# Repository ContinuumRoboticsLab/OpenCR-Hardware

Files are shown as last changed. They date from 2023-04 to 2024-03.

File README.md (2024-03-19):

# OpenCR-Hardware

Here we provide CAD design, component lists, assembly instructions, and software for you to create your continuum robot.
The prototypes, parts of them, and extensions can be used to build torque-controlled continuum robot prototypes.
A paper describing the actuation module and three different derived prototypes can be found [here](https://arxiv.org/abs/2304.11850).

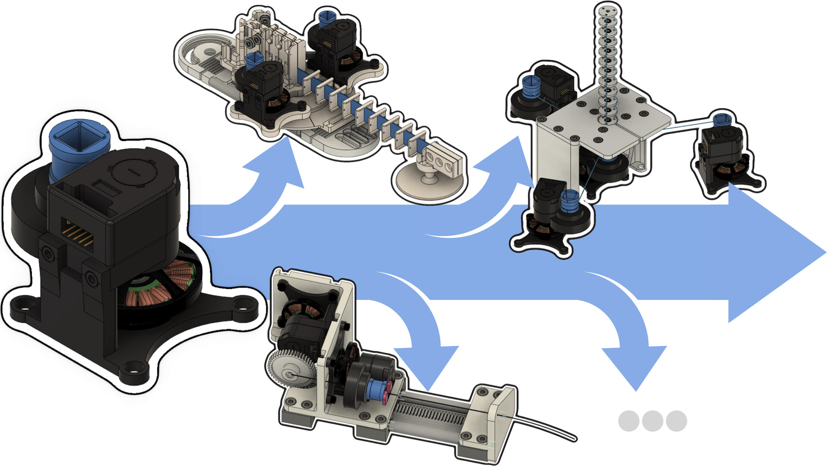
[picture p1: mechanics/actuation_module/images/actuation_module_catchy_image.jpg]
catchy overview


*Figure: An actuation module for a wide range of continuum robots*

## Electronics

| TI Evaluation Board                                                                                                       | Consumer PC | Details Wiring |  
|---------------------------------------------------------------------------------------------------------------------------|-------------|----------------|   
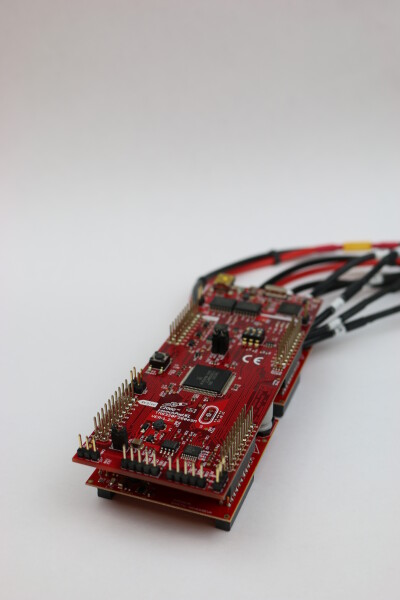
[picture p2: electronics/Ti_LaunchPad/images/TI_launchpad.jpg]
|  | WIP         | WIP            |

## Mechanics

| Concentric Tube Continuum Robot (LOTR CTCR)                                                                             | spatial Tendon-Driven Continuum Robot (LOTR TDCR)                                                                                    | parallel Tendon-Driven Continuum Robot (LOTR TDCR)                                                                                |  
|-------------------------------------------------------------------------------------------------------------------------|--------------------------------------------------------------------------------------------------------------------------------------|-----------------------------------------------------------------------------------------------------------------------------------|   
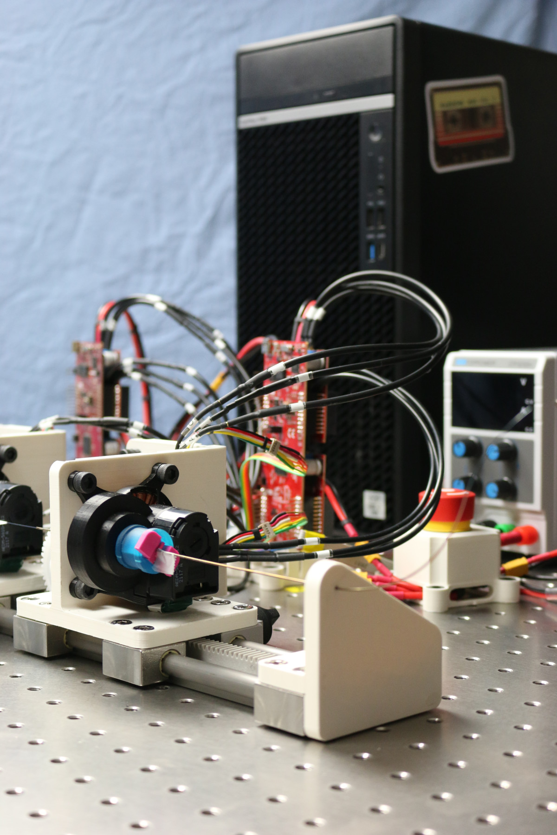
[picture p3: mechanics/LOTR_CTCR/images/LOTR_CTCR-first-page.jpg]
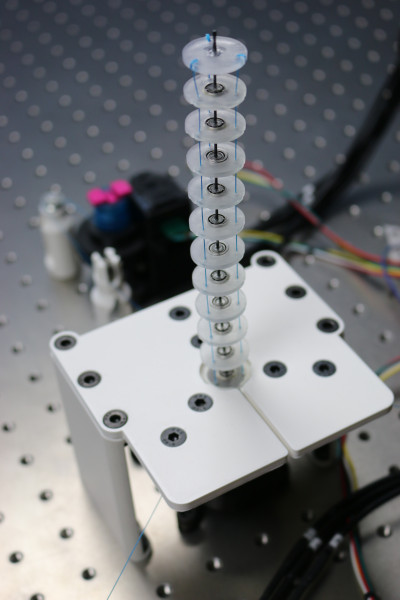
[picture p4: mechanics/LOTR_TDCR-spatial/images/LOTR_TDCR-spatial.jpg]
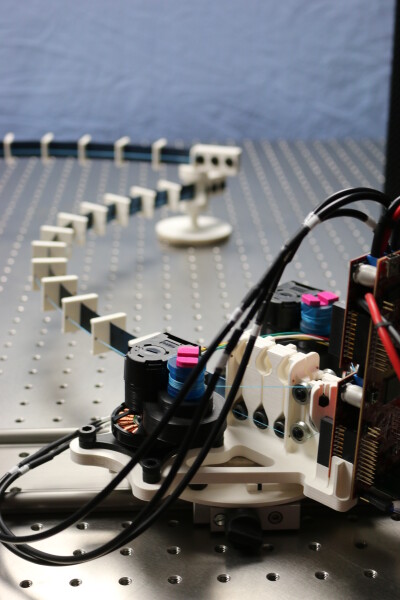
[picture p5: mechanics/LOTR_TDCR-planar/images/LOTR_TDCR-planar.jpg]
|  |  |  |

## More Information

### Further Links

[OpenCR Project](http://opencontinuumrobotics.ca)
<br/>
[Back to Top of Page](README.md)
<br/>
[Electronic Overview](electronics/README.md)
<br/>
[Hardware Overview](mechanics/README.md)

### Authors

Authors are listed in alphabetic order.

- Reinhard M. Grassmann

### License

BSD 3-Clause License

Copyright (c) 2023, Continuum Robotics Laboratory, University of Toronto

### BibTeX

This repository is part of the [OpenCR Project](http://www.opencontinuumrobotics.ca/) and different publications.
If you want to reference this project, you can use the following citation:

```bibtex
    @article{GrassmannBurgner-Kahrs_et_al_Frontiers_2023,
        title       =   {Open Continuum Robotics – One Actuation Module to Create them All},
        author      =   {Grassmann, Reinhard M. and Shentu, Chengnan and Hamoda, Taqi and Triana Dewi, Puspita and Burgner-Kahrs, Jessica},
        journal     =   {Frontiers in Robotics and AI},
        volume      =   {11},
        pages       =   {1272403},
        year        =   {2024},
        doi         =   {10.3389/frobt.2024.1272403}
    }
```
We took great inspiration from the [Open Dynamic Robot Initiative](https://open-dynamic-robot-initiative.github.io/), where efforts are made to build cost-efficient actuators for torque-controlled [legged robots](https://arxiv.org/abs/1910.00093) and [manipulators](https://arxiv.org/abs/2008.03596).

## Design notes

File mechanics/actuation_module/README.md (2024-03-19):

# OpenCR-Hardware Actuation Module

## Electronics Overview

WIP

## Mechanics Overview

WIP

### 3D Printed Parts

WIP

### Off-the-shelf Components

WIP

### Step-by-Step Instructions

WIP

## Bill of Materials for one Actuation Module

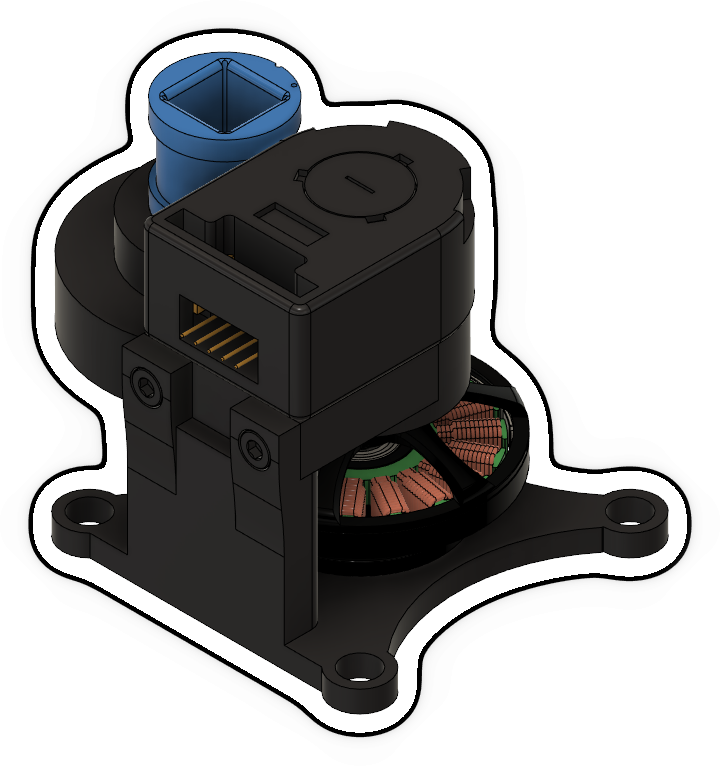
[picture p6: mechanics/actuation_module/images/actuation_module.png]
catchy overview


| Part Name                         | Quantity | Notes                                                                | File/Link                                                                                                            |  
|-----------------------------------|----------|----------------------------------------------------------------------|----------------------------------------------------------------------------------------------------------------------|   
| ActuationUnit_MotorSide_Cube      | 1        | 3D printed part ([drawing](drawings/Motor_Frame.pdf))                | [STL file](stl_files/ActuationUnit_EncoderCouplingSide.stl)                                                          |
| Motor                             | 1        | T-Motor MN4004                                                       | [External link](https://store.tmotor.com/goods-438-Antigravity+MN4004+KV300+-+2PCSSET.html)                          |
| Gear_Motor                        | 1        | McMaster Carr (P/N 2662N313)                                         | [External link](https://www.mcmaster.com/2662N313/)                                                                  |
| Gear_Encoder                      | 1        | McMaster Carr (P/N 2662N321)                                         | [External link](https://www.mcmaster.com/2662N321/)                                                                  |
| ActuationUnit_EncoderCouplingSide | 1        | 3D printed part ([drawing](drawings/Encoder_Frame.pdf))              | [STL file](stl_files/ActuationUnit_MotorSide_Cube.stl)                                                               |
| Ball Bearing                      | 2        | McMaster Carr (P/N 5972K910)                                         | [External link](https://www.mcmaster.com/5972K91/)                                                                   |
| Shaft_GearCoupling                | 1        | 3D printed part ([drawing](drawings/Shaft_GearCoupling_Drawing.pdf)) | [STL file](stl_files/Shaft_GearCoupling.stl)                                                                         |
| Shaft_MotorEncoder                | 1        | 3D printed part ([drawing](Shaft_MotorEncoder_Drawing.pdf))          | [STL file](stl_files/Shaft_MotorEncoder.stl)                                                                         |
| Screw M3x10                       | 2        | McMaster Carr (P/N 91290A115)                                        | [External link](https://www.mcmaster.com/91290A115/)                                                                 |
| Nut M3                            | 2        | McMaster Carr (P/N 90593A001)                                        | [External link](https://www.mcmaster.com/90593A001/)                                                                 |
| Encoder                           | 1        | Avago AEDM-5810                                                      | [External link](https://www.mouser.ca/ProductDetail/Broadcom-Avago/AEDM-5810-Z12?qs=nm95cbFn36yryX%2Fd2Onjlw%3D%3D ) |

## More Information

### Further Links

[OpenCR Project](http://opencontinuumrobotics.ca)
<br/>
[Back to Top of Page](README.md)
<br/>
[Electronic Overview](electronics/README.md)
<br/>
[Hardware Overview](mechanics/README.md)

### Authors

Authors are listed in alphabetic order.

- Puspita Triana Dewi
- Reinhard M. Grassmann

### License

BSD 3-Clause License

Copyright (c) 2023, Continuum Robotics Laboratory, University of Toronto

### BibTeX

This design is part of the [OpenCR Project](http://www.opencontinuumrobotics.ca/).
If you want to reference this design, you can use the following citation:

```bibtex
    @article{GrassmannBurgner-Kahrs_et_al_Frontiers_2023,
        title       =   {Open Continuum Robotics – One Actuation Module to Create them All},
        author      =   {Grassmann, Reinhard M. and Shentu, Chengnan and Hamoda, Taqi and Triana Dewi, Puspita and Burgner-Kahrs, Jessica},
        journal     =   {Frontiers in Robotics and AI},
        volume      =   {11},
        pages       =   {1272403},
        year        =   {2024},
        doi         =   {10.3389/frobt.2024.1272403}
    }
```

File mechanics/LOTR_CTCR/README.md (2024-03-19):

# Concentric Tube Continuum Robot Prototype

Concentric tube continuum robots (CTCR) are a class of continuum robots.
A CTCR consists of multiple nested tubes that are concentric, pre-curved, and super-elastic. 
To generate a motion by changing the centerline of the nested tubes, each tube can be rotated and translated.
The rotational and translational motion can be generated by using two independent motors attached to a carriage. 
We refer to the survey by [Nwafor, Rabenorosoa et al. (T-RO 2023)](https://doi.org/10.1109/TRO.2023.3255512) for a general overview on CTCRs. 

We developed a torque-controlled CTCR with low complexity.
It is shown in the image below.

<p float="left">
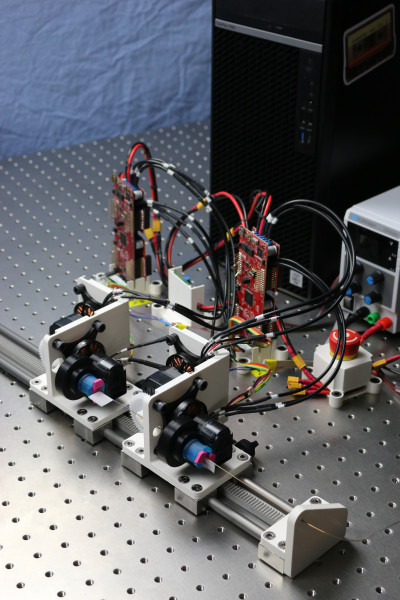
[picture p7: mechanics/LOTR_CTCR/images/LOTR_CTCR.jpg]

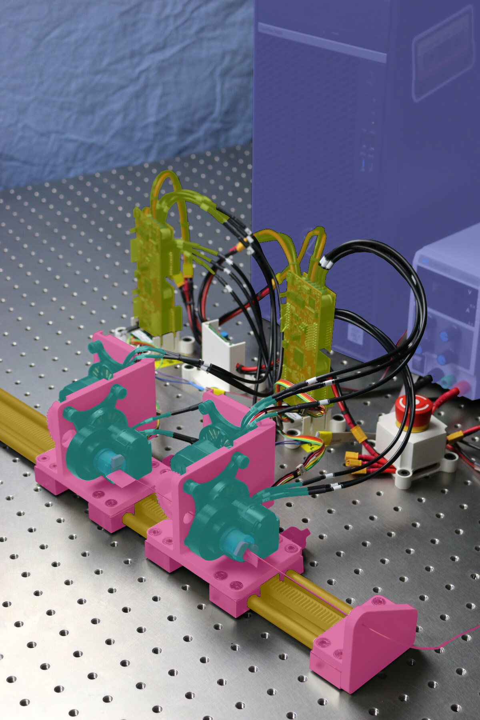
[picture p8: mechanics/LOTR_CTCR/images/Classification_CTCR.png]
classification overview

</p>

*Figure: Image of a CTCR with two carriages. Right images shows a classification of the component. (cyan) actuation modules, (red) frames, (yellow) guiding rail, (green) evaluation boards, and (blue) consumer pc with power supply.*

## Electronics Overview

WIP

## Mechanics Overview

WIP

### Tubes

Note that we do not provide tubes.
In general, the flexible tubes are made of a Nitinol or made of thermoplastic materials in some instances. 
The material can be arbitrary as long as the elastic interaction between the tubes can be exploited.
For example

- Thermoplastic material [Amanov, Nguyen & Burgner-Kahrs (SPIE 2015)](https://doi.org/10.1117/12.2081999) and [Morimoto & Okamura (T-RO 2016)](https://doi.org/10.1109/TRO.2016.2602368)
- Nitinol [Sears & Dupont (IROS 2006)](https://doi.org/10.1109/IROS.2006.282072) and [Webster, Okamura & Cowan (IROS 2006)](https://doi.org/10.1109/IROS.2006.282073)

Further references are provided in [Nwafor, Rabenorosoa et al. (T-RO 2023)](https://doi.org/10.1109/TRO.2023.3255512). 
    
We ordered our pre-curved Nitinol tubes from [Euroflex GmbH (Nuernberg, Germany)](https://www.euroflex.de/en/index.html).

### 3D Printed Parts

WIP

### Off-the-shelf Components

WIP

### Bill of Materials for Concentric Tube Continuum Robot Prototype

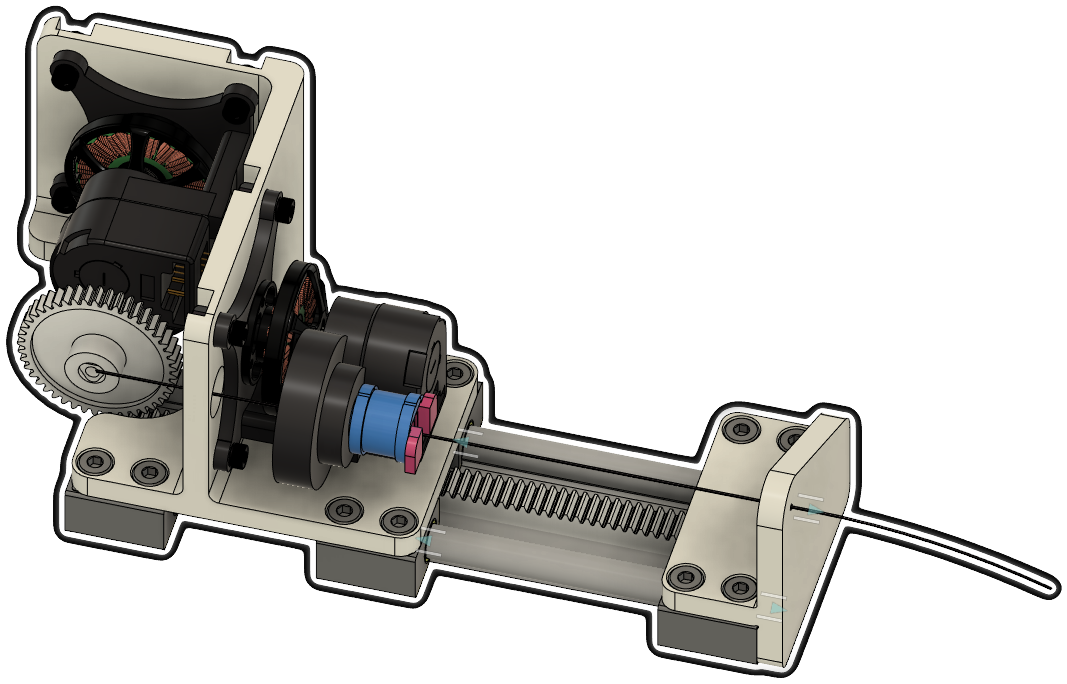
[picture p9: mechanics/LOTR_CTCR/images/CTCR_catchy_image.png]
catchy overview


| Part Name            | Quantity | Notes                                                           | File/Link                                                                                            |  
|----------------------|----------|-----------------------------------------------------------------|------------------------------------------------------------------------------------------------------|   
| Actuation Module     | 2        |                                                                 | [Link](https://github.com/ContinuumRoboticsLab/OpenCR-Hardware/tree/main/mechanics/actuation_module) |
| Main_Frame           | 1        | 3D printed part ([drawing](drawings/Main_Frame_drawing.pdf))    | [STL file](stl_files/Main_Frame.stl)                                                                 |
| Front_Frame          | 1        | 3D printed part ([drawing](drawings/Front_Frame_drawing.pdf))   | [STL file](stl_files/Front_Frame.stl)                                                                |
| Cap Gear             | 1        | 3D printed part ([drawing](drawings/Cap_Gear_8mm_drawing.pdf))  | [STL file](stl_files/Cap_Gear_8mm.stl)                                                               |
| Tube Cap             | 1        | 3D printed part ([drawing](drawings/Tube_coppling_drawing.pdf)) | [STL file](stl_files/Tube_Cap.stl)                                                                   |
| Rail                 | 1        | Igus (P/N WS-10-40))                                            | [External Link](https://www.igus.eu/product/732?artNr=WS-10-40)                                      |
| Pillow Block         | 6        | Igus (P/N WJ200UM-01-10-AL)                                     | [External Link](https://www.igus.ca/product/1165?artNr=WJ200UM-01-10-AL)                             |
| Gear Rack            | 1        | McMaster-Carr (P/N 2662N57)                                     | [External Link](https://www.mcmaster.com/2662N57/)                                                   |
| Gear                 | 1        | McMaster-Carr (P/N 2662N42)                                     | [External Link](https://www.mcmaster.com/2662N42/)                                                   |
| M6x14 Screw          | 20       | McMaster-Carr (P/N 91290A319)                                   | [External Link](https://www.mcmaster.com/91290A319/)                                                 |
| M6 Nut               | 8        | McMaster-Carr (P/N 90593A005)                                   | [External Link](https://www.mcmaster.com/90593A005/)                                                 |
| Pre-curved NiTi Tube | 1        | Euroflex                                                        | [External Link](https://www.euroflex.de/en/index.html)                                               |

## Step-by-Step Instructions

Step 1: Assemble the [gear rack](https://www.mcmaster.com/2662N57/) onto the [rail](https://www.igus.eu/product/732?artNr=WS-10-40).

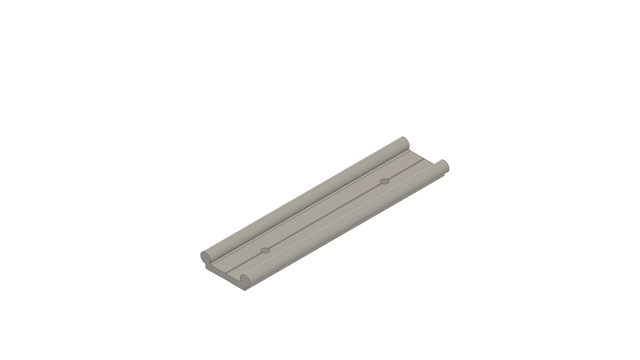
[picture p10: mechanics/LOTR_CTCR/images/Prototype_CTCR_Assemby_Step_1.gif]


Step 2: Assemble 4 [pillow blocks](https://www.igus.ca/product/1165?artNr=WJ200UM-01-10-AL) onto the rail. 

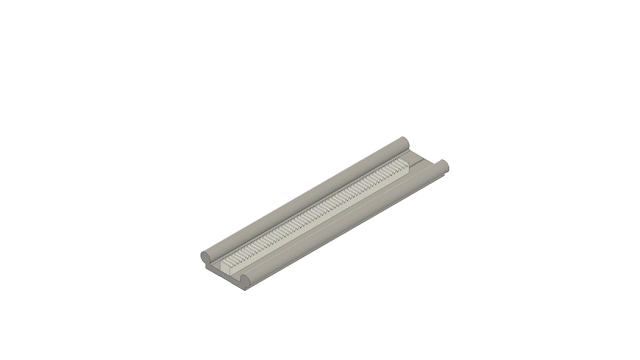
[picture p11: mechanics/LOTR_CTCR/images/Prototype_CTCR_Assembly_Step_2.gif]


Step 3: Assemble the [main frame](stl_files/Main_Frame.stl) to the rail system with 8 [M6x14 screws](https://www.mcmaster.com/91290A319/).

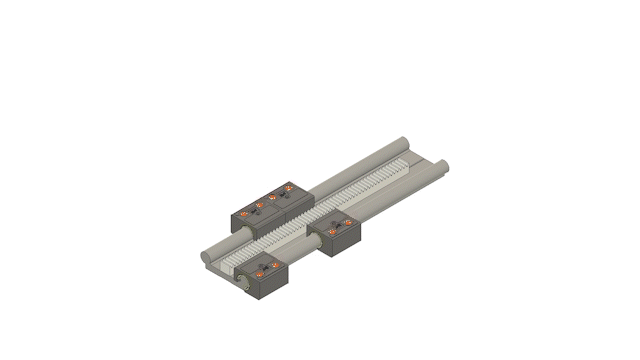
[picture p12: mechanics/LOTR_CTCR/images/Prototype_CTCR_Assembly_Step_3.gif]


Step 4: Assemble 2 [actuation modules](https://github.com/ContinuumRoboticsLab/OpenCR-Hardware/tree/main/mechanics/actuation_module) to the main frame with 4 [M6x14 screws](https://www.mcmaster.com/91290A319/) and 4 [M6 nuts](https://www.mcmaster.com/90593A005/) for each actuation module.

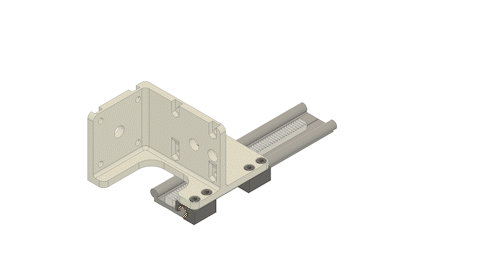
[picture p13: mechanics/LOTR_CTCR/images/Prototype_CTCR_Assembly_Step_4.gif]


Step 5: Assemble the [gear](https://www.mcmaster.com/2662N42/) to the rear actuation module using the [cap gear](stl_files/Cap_Gear_8mm.stl).

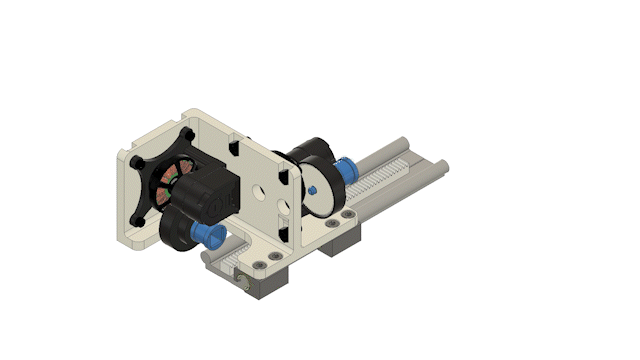
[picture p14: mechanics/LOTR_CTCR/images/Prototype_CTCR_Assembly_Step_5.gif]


Step 6: Assemble the [front frame](stl_files/Front_Frame.stl) to the rail system with 8 [M6x14 screws](https://www.mcmaster.com/91290A319/).

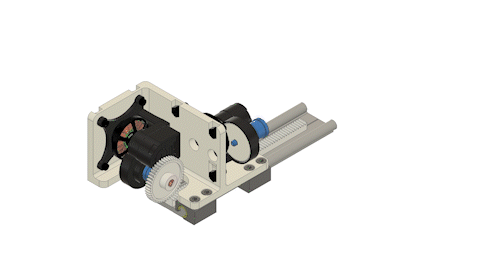
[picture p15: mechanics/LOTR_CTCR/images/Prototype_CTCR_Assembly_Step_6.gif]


Step 7: Assemble the [pre-curved Nitinol tube](https://www.euroflex.de/en/index.html) to the front actuation module using the [tube cap](stl_files/Tube_Cap.stl).

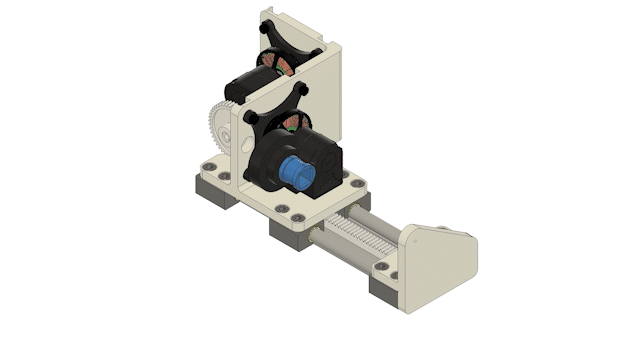
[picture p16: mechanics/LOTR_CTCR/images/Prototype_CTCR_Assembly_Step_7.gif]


## More Information

### Further Links

[OpenCR Project](http://opencontinuumrobotics.ca)
<br/>
[Back to Top of Page](README.md)
<br/>
[Electronic Overview](electronics/README.md)
<br/>
[Hardware Overview](mechanics/README.md)

### Authors

Authors are listed in alphabetic order.

- Puspita Triana Dewi
- Reinhard M. Grassmann

### License

BSD 3-Clause License

Copyright (c) 2023, Continuum Robotics Laboratory, University of Toronto

### BibTeX

This design is part of the [OpenCR Project](http://www.opencontinuumrobotics.ca/).
If you want to reference this design, you can use the following citation:

```bibtex
    @article{GrassmannBurgner-Kahrs_et_al_Frontiers_2023,
        title       =   {Open Continuum Robotics – One Actuation Module to Create them All},
        author      =   {Grassmann, Reinhard M. and Shentu, Chengnan and Hamoda, Taqi and Triana Dewi, Puspita and Burgner-Kahrs, Jessica},
        journal     =   {Frontiers in Robotics and AI},
        volume      =   {11},
        pages       =   {1272403},
        year        =   {2024},
        doi         =   {10.3389/frobt.2024.1272403}
    }
```

### Trivia

LOTR stands for Lord of the Ring, in reference to the title of the paper. Yes, the movie.

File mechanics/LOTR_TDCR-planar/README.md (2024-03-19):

# Planar Tendon-Driven Continuum Robot Prototype

A parallel continuum robot (PCR) tries to combine the world of rigid parallel robots and continuum robots.
This one is a planar PCR, where the beam is tendon-actuated.
It has two bases rigid linked at the distal end of the beam.

<p float="left">
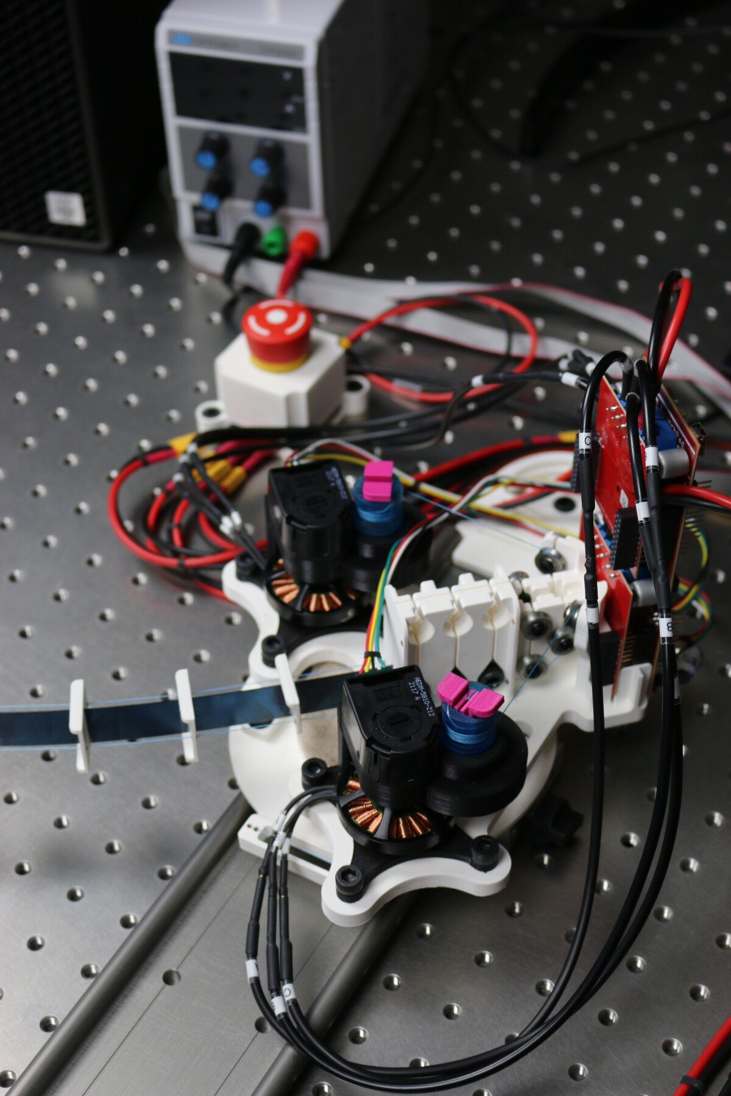
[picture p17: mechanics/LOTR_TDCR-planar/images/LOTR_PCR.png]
catchy overview

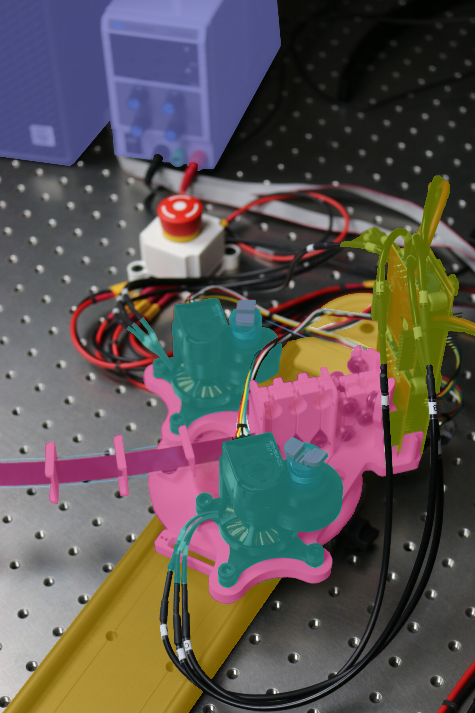
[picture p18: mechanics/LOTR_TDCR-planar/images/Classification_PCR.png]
classification overview

</p>

*Figure: Image of one base of the PCR. Right images shows a classification of the component. (cyan) actuation modules, (red) frames, (green) evaluation boards, (yellow) guiding rail, and (blue) consumer pc with power supply.*

## Electronics Overview

WIP

## Mechanics Overview

WIP

### 3D Printed Parts

WIP

### Off-the-shelf Components

WIP

### Step-by-Step Instructions

WIP

### Bill of Materials for Planar Tendon-Driven Continuum Robot Prototype 

| Part Name                       | Quantity | Notes                                                                        | File/Link                                                                                                                                                                                                                    |  
|---------------------------------|----------|------------------------------------------------------------------------------|------------------------------------------------------------------------------------------------------------------------------------------------------------------------------------------------------------------------------|   
| Actuation Module                | 2        |                                                                              | [Link](https://github.com/ContinuumRoboticsLab/OpenCR-Hardware/tree/main/mechanics/actuation_module)                                                                                                                         |
| Turret Frame                    | 1        | 3D printed part ([drawing](drawings/Frame_turret_drawing.pdf))               | [STL file](stl_files/frame_turret.stl)                                                                                                                                                                                       |
| Base Plate                      | 1        | 3D printed part ([drawing](drawings/Frame_base_plate_drawing.pdf))           | [STL file](stl_files/frame_base_plate.stl)                                                                                                                                                                                   |
| Glider                          | 1        | 3D printed part ([drawing](drawings/EE_glider_small_drawing.pdf))            | [STL file](stl_files/EE_glider_small.stl)                                                                                                                                                                                    |
| Spacer Disk                     | 9        | 3D printed part ([drawing](drawings/Spacer_Disk_drawing.pdf))                | [STL file](stl_files/spacer_disk.stl)                                                                                                                                                                                        |
| End Effector                    | 1        | 3D printed part ([drawing](drawings/EE_middle_drawing.pdf))                  | [STL file](stl_files/EE_middle.stl)                                                                                                                                                                                          |
| Rail-to-Table Connector (Right) | 1        | 3D printed part ([drawing](drawings/rail2table_connector_right_drawing.pdf)) | [STL file](stl_files/rail2table_connector_right.stl)                                                                                                                                                                         |
| Rail-to-Table Connector (Left)  | 1        | 3D printed part ([drawing](drawings/Rail2table_connector_left_drawing.pdf))  | [STL file](stl_files/rail2table_connector_left.stl)                                                                                                                                                                          |
| Felt Pad                        | 1        | Off-the-shelf component (Amazon)                                             | [External Link](https://www.amazon.ca/Scotch-SP828-NA-Round-Furniture-Brown/dp/B01MTMXCGC/ref=sr_1_4?crid=2CS0CEP2WS7PA&keywords=felt%2Bpads%2B3%22&qid=1685066557&s=hi&sprefix=felt%2Bpads%2B3%2B%2Ctools%2C89&sr=1-4&th=1) |
| Pulley                          | 8        | Off-the-shelf component (Amazon)                                             | [External Link](https://www.amazon.ca/V623ZZ-Groove-Bearing-Carbon-3x12x4mm/dp/B07CV8CW1F)                                                                                                                                   |
| Rail                            | 1        | Igus (P/N WS-10-40)                                                          | [External Link](https://www.igus.eu/product/732?artNr=WS-10-40)                                                                                                                                                              |
| Pillow Block                    | 4        | Igus (P/N WJ200UM-01-10-AL)                                                  | [External Link](https://https://www.igus.ca/product/1165?artNr=WJ200UM-01-10-AL)                                                                                                                                             |
| M6x14 Screw                     | 12       | McMaster-Carr (P/N 91290A319)                                                | [External Link](https://www.mcmaster.com/91290A319/)                                                                                                                                                                         |
| M6 Nut                          | 8        | McMaster-Carr (P/N 90593A005)                                                | [External Link](https://www.mcmaster.com/90593A005/)                                                                                                                                                                         |
| Beam                            | 1        | McMaster-Carr (P/N 9075K79)                                                  | [External Link](https://www.mcmaster.com/9075K79/)                                                                                                                                                                           |
| Tendon                          | 2        | McMaster-Carr (P/N 9442T4)                                                   | [External Link](https://www.mcmaster.com/9442T4/)                                                                                                                                                                            |

## More Information

### Further Links

[OpenCR Project](http://opencontinuumrobotics.ca)
<br/>
[Back to Top of Page](README.md)
<br/>
[Electronic Overview](electronics/README.md)
<br/>
[Hardware Overview](mechanics/README.md)

### Authors

Authors are listed in alphabetic order.

- Puspita Triana Dewi
- Reinhard M. Grassmann

### License

BSD 3-Clause License

Copyright (c) 2023, Continuum Robotics Laboratory, University of Toronto

### BibTeX

This design is part of the [OpenCR Project](http://www.opencontinuumrobotics.ca/).
If you want to reference this design, you can use the following citation:

```bibtex
    @article{GrassmannBurgner-Kahrs_et_al_Frontiers_2023,
        title       =   {Open Continuum Robotics – One Actuation Module to Create them All},
        author      =   {Grassmann, Reinhard M. and Shentu, Chengnan and Hamoda, Taqi and Triana Dewi, Puspita and Burgner-Kahrs, Jessica},
        journal     =   {Frontiers in Robotics and AI},
        volume      =   {11},
        pages       =   {1272403},
        year        =   {2024},
        doi         =   {10.3389/frobt.2024.1272403}
    }
```

### Trivia

LOTR stands for Lord of the Ring, in reference to the title of the paper. Yes, the movie.

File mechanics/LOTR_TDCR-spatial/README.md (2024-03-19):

# Spatial Tendon-Driven Continuum Robot Prototype

A tendon-driven continuum robot (TDCR) is composed of a flexible backbone along which tendons are guided using spacer disks, these last ones being fixed to the backbone. 
It is actuated by changing the tendons’ length and applying tendon tensions, which cause a reversible deformation of the backbone.
This one has one [type-II segment](https://www.frontiersin.org/articles/10.3389/frobt.2022.873446/full) and three tendons.

<p float="left">
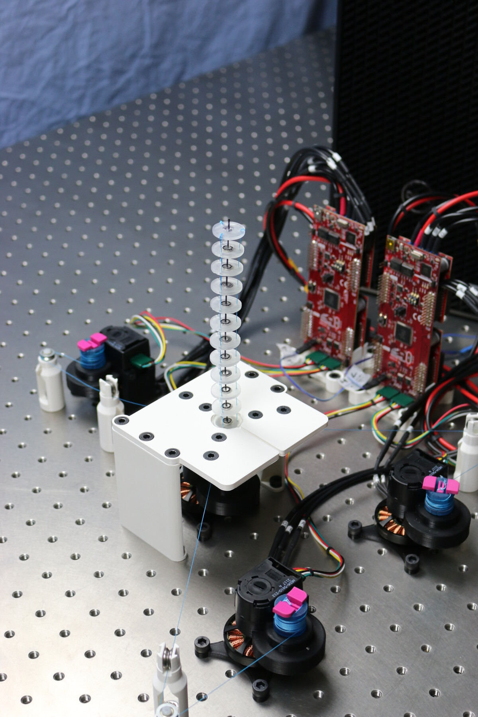
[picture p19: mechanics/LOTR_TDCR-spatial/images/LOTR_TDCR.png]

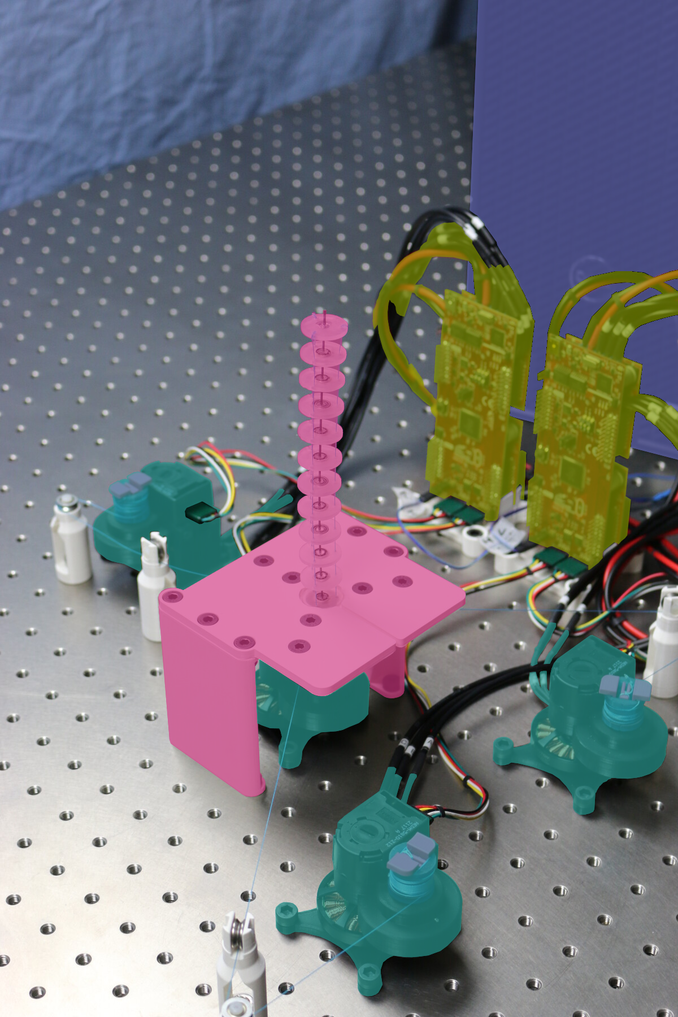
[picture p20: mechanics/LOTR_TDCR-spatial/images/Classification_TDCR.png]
classification overview

</p>

*Figure: Image of a TDCR with three degrees of freedom. Right images shows a classification of the component. (cyan) actuation modules, (red) frames, (green) evaluation boards, and (blue) consumer pc with power supply.*

## Electronics Overview

WIP

## Mechanics Overview

WIP

## 3D Printed Parts

WIP

## Off-the-shelf Components

WIP

## Bill of Materials for Spatial Tendon-Driven Continuum Robot Prototype

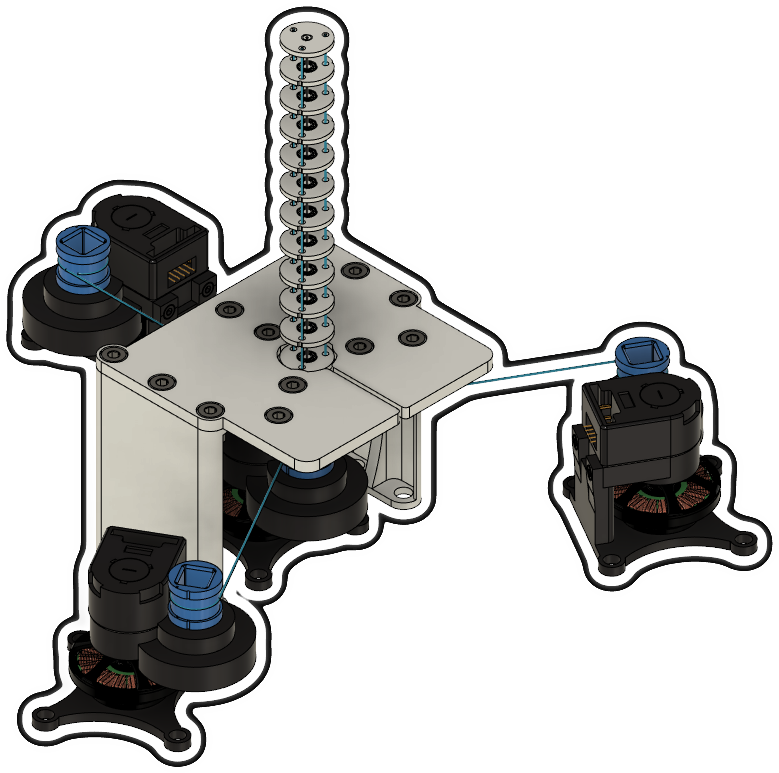
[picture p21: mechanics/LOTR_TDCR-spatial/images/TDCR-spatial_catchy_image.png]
catchy overview


| Part Name            | Quantity | Notes                                                                          | File/Link                                                                                            |  
|----------------------|----------|--------------------------------------------------------------------------------|------------------------------------------------------------------------------------------------------|   
| Actuation Module     | 4        |                                                                                | [Link](https://github.com/ContinuumRoboticsLab/OpenCR-Hardware/tree/main/mechanics/actuation_module) |
| Base Platform        | 1        | 3D printed part ([drawing](drawings/BasePlatform_drawing.pdf))                 | [STL file](stl_files/BasePlatform.stl)                                                               |
| Base Platform Wall   | 2        | 3D printed part ([drawing](drawings/BasePlatform_wall_drawing.pdf))            | [STL file](stl_files/BasePlatform_wall.stl)                                                          |
| Pulley Holder        | 3        | 3D printed part ([drawing](drawings/BasePlatform_PullyHolder_Drawing.pdf))     | [STL file](stl_files/BasePlatform_PullyHolder.stl)                                                   |
| Pulley Shaft         | 6        | 3D printed part ([drawing](drawings/Shaft_pulley_drawing.pdf))                 | [STL file](stl_files/BasePlatform_PulleyShaft.stl)                                                   |
| Disk without Dent    | 1        | 3D printed part ([drawing](drawings/FSD_20mm_bearing_withoutDent_Drawing.pdf)) | [STL file](stl_files/FSD_20mm_bearing_withoutDent.stl)                                               |
| Disk                 | 10       | 3D printed part ([drawing](drawings/Disk_drawing v1.pdf))                      | [STL file](stl_files/FSD_20mm_bearing.stl)                                                           |
| End Disk             | 1        | 3D printed part ([drawing](drawings/FSDzero_20mm_withoutDent_drawing.pdf))     | [STL file](stl_files/FSDzero_20mm.stl)                                                               |
| Inner Disk           | 12       | 3D printed part ([drawing](drawings/FSD_bearing_inner_Drawing.pdf))            | [STL file](stl_files/FSD_bearing_inner.stl)                                                          |
| Tube Coupling        | 1        | 3D printed part ([drawing](drawings/Tube_coppling_1mm_drawing.pdf))            | [STL file](stl_files/Tube_coppling_1mm.stl)                                                          |
| Bearing              | 11       | McMaster-Carr (P/N 57155K438)                                                  | [External link](https://www.mcmaster.com/57155K438/)                                                 |
| Backbone (NiTi Tube) | 1        | Off-the-shelf component                                                        |                                                                                                      |
| Tendon               | 1        | McMaster-Carr (P/N 9442T4)                                                     | [External link](https://www.mcmaster.com/9442T4/)                                                    |
| Pulley               | 6        | Off-the-shelf component (Amazon)                                               | [External link](https://www.amazon.ca/V623ZZ-Groove-Bearing-Carbon-3x12x4mm/dp/B07CV8CW1F)           |
| M6x8 Screw           | 12       | McMaster-Carr (P/N 93070A139)                                                  | [External link](https://www.mcmaster.com/93070A139/)                                                 |
| M6 Nut               | 12       | McMaster-Carr (P/N 90593A005)                                                  | [External link](https://www.mcmaster.com/90593A005/)                                                 |

## Step-by-Step Instructions

Step 1: Assemble 2 [pulleys](https://www.amazon.ca/V623ZZ-Groove-Bearing-Carbon-3x12x4mm/dp/B07CV8CW1F) into the puley [holder](stl_files/BasePlatform_PullyHolder.stl) with [pulley shaft](stl_files/BasePlatform_PulleyShaft). Do this for 3 sets of pulley systems.

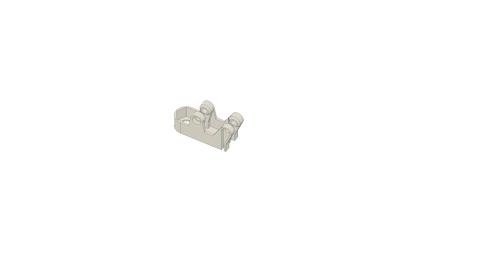
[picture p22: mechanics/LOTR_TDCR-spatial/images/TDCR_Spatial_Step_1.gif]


Step 2: Assemble the pulley system to the bottom side of the [base platform](stl_files/BasePlatform.stl) using [M6 screws](https://www.mcmaster.com/93070A139/) and [M6 nuts](https://www.mcmaster.com/90593A005/).

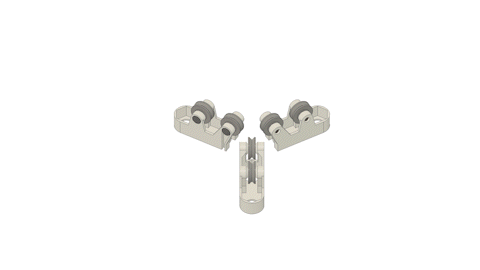
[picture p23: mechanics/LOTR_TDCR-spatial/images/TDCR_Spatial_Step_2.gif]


Step 3: Assemble the [base platform](stl_files/BasePlatform.stl) to the [base platform wall](stl_files/BasePlatform_wall.stl) using [M6 screws](https://www.mcmaster.com/93070A139/) and [M6 nuts](https://www.mcmaster.com/90593A005/).

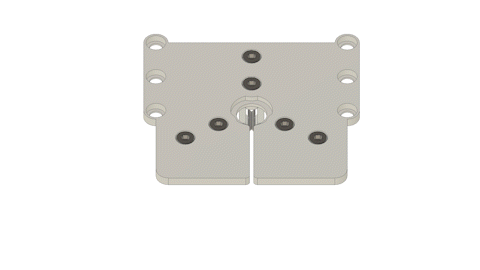
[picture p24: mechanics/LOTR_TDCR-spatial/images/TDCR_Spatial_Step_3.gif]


Step 4: Insert the [inner disk](stl_files/FSD_bearing_inner.stl) into the [end disk](stl_files/FSDzero_20mm.stl).

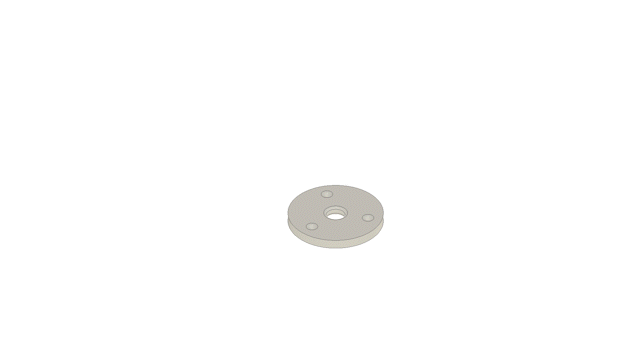
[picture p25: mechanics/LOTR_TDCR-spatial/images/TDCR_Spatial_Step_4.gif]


Step 5: Insert the [inner disk](stl_files/FSD_bearing_inner.stl) into the [bearing](https://www.mcmaster.com/57155K438/). Do this for 11 sets of bearings.

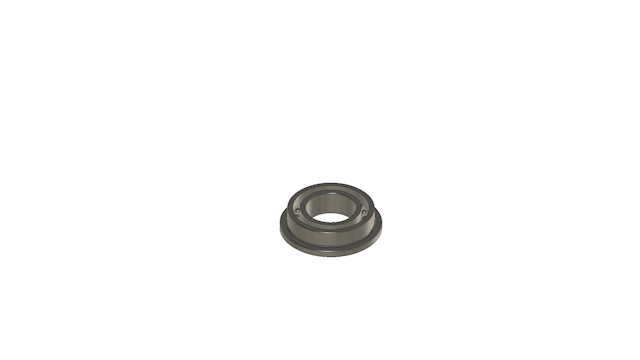
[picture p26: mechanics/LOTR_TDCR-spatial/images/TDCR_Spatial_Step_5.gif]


Step 6: Insert the bearing into 10 [disks](stl_files/FSD_20mm_bearing.stl) and 1 [disk without dent](stl_files/FSD_20mm_bearing_withoutDent.stl).

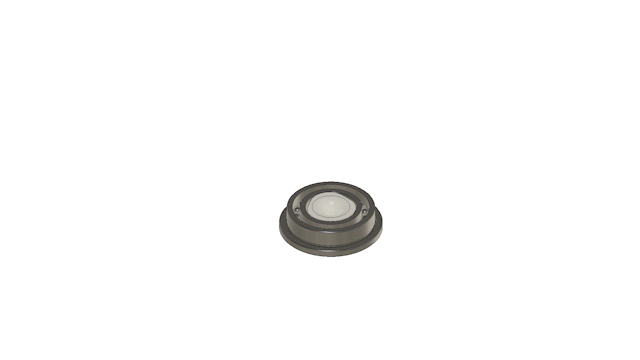
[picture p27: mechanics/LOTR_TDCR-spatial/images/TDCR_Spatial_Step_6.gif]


Step 7: Arrange the disks to the backbone in equidistant. The arrangement should be (from top to bottom) end disk --> 10 disks --> disk without dent. Make sure that the tendon holes are in a straight line from top to the bottom.

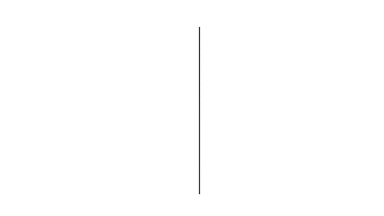
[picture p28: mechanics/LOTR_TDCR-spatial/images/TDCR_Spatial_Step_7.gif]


Step 8: Route the tendon along the tendon holes. Tie a knot at the end disk as a determination point. Do this for 3 sets of tendons.

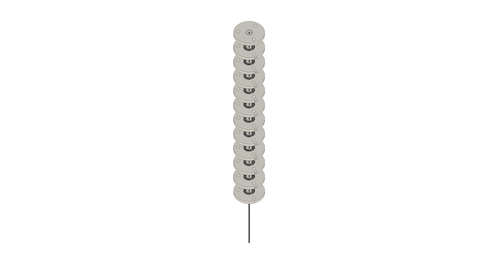
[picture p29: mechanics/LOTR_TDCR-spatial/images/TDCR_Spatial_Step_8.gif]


Step 9: Assemble the continuum robot to the base platform using [M6 screws](https://www.mcmaster.com/93070A139/) and [M6 nuts](https://www.mcmaster.com/90593A005/).



Step 10: Assemble the backbone to the [actuation module](https://github.com/ContinuumRoboticsLab/OpenCR-Hardware/tree/main/mechanics/actuation_module) using [tube coupling](stl_files/Tube_coppling_1mm.stl).



Step 11: Attach each tendon to one [actuation module](https://github.com/ContinuumRoboticsLab/OpenCR-Hardware/tree/main/mechanics/actuation_module) though the pulley system.



## More Information

### Further Links

[OpenCR Project](http://opencontinuumrobotics.ca)
<br/>
[Back to Top of Page](README.md)
<br/>
[Electronic Overview](electronics/README.md)
<br/>
[Hardware Overview](mechanics/README.md)

### Authors

Authors are listed in alphabetic order.

- Puspita Triana Dewi
- Reinhard M. Grassmann

### License

BSD 3-Clause License

Copyright (c) 2023, Continuum Robotics Laboratory, University of Toronto

### BibTeX

This design is part of the [OpenCR Project](http://www.opencontinuumrobotics.ca/).
If you want to reference this design, you can use the following citation:

```bibtex
    @article{GrassmannBurgner-Kahrs_et_al_Frontiers_2023,
        title       =   {Open Continuum Robotics – One Actuation Module to Create them All},
        author      =   {Grassmann, Reinhard M. and Shentu, Chengnan and Hamoda, Taqi and Triana Dewi, Puspita and Burgner-Kahrs, Jessica},
        journal     =   {Frontiers in Robotics and AI},
        volume      =   {11},
        pages       =   {1272403},
        year        =   {2024},
        doi         =   {10.3389/frobt.2024.1272403}
    }
```

### Trivia

LOTR stands for Lord of the Ring, in reference to the title of the paper. Yes, the movie.

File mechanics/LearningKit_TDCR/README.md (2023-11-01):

# Learning Kit for Tendon-driven Continuum Robot Prototype

A tendon-driven continuum robot (TDCR) is composed of a flexible backbone along which tendons are guided using spacer disks, these last ones being fixed to the backbone. 
It is actuated by changing the tendons’ length and applying tendon tensions, which cause a reversible deformation of the backbone.
This prototype has a segment with [type-II spacer disks (Grassmann et al., FRobt 2022)](https://www.frontiersin.org/articles/10.3389/frobt.2022.873446/full) and three tendons.

<p float="left">
CAD image of learning kit
foto of learning kif
</p>

*Figure: CAD image and foto of a Learning Kit.*

## Electronics Overview

WIP

## Mechanics Overview

<p float="left">
CAD image of learning kit
</p>
The manipulator of the TDCR consists of 10 type-II spacer disks equally distributed along a Nitinol Backbone with a diameter of 1.4 mm. 
The robot is capable of 3 DOFs, namely bending across two planes and rotation about its axis. 
Three independently actuated tendons made of Spectra Fiber and an actuator to rotate the backbone are used to enable these degrees of freedom. 

<p float="left">
CAD image of learning kit
</p>

The body of the spacer disk is fixed to the backbone axially, while a bearing in the middle enables the rotational DOF. 
It is split into two parts to enable the insertion of the bearing in the middle. 
I changed the regular ball bearing to a pulley to reduce the number of unique components. 
The profile of the two parts allows for easy assembly while ensuring that the actuation through the tendons is optimal. 
The grooves ensure the adhesive stays inside the segment and does not spill out. 
The FSD Backbone Clamp functions as a spacer to make the pulley bore smaller. 
It is designed with a unique profile that balances the required friction to grip the backbone and the need for a constant curvature. 

<p float="left">
CAD image of learning kit
</p>

All components are placed inside a hexagonal casing with windows made of transparent acrylic sheets to view the system’s working. 
The three tendon actuators are fixed horizontally to reduce tendon routing. 
Six pulleys are placed inside to help reduce the tendon offset and increase the efficiency of tendon control. 
An actuation module is placed at the bottom and controls backbone rotation. 
To secure the electric components in the case, custom 3D-printed mounts have been designed. 
All components are placed in a way visible from the windows to allow the user to see the robot’s functioning, allowing better understanding and enabling the development of intuition.

<p float="left">
CAD image of learning kit
</p>

The previously used [actuation module (Grassmann et al., ArXiv 2023)](https://www.frontiersin.org/articles/10.3389/frobt.2022.873446/full) was modified to suit this kit’s requirements. 
The multipart casing is replaced with a single unit. 
A new casing is designed to be easier to manufacture and maintain adequate performance. 
The assembly process is simplified as the singular casing eliminates input and output shaft misalignment. 
The motor and the gears can easily fit into designated spaces using dedicated slots. 
Since the actuator will only actuate tendons, an extra bearing is introduced at the output shaft to handle the increased radial tension and eliminate shaft eccentricity. 

## Bill of Materials for Spatial Tendon-Driven Continuum Robot Prototype

| Part Name                          | Quantity | Notes                            | File/Link                                                                                                           |
|------------------------------------|----------|----------------------------------|---------------------------------------------------------------------------------------------------------------------|
| Base Casing                        | 1        | 3D Printed Part                  | [STL File](stl_files/Base_Casing.stl)                                                                               |
| Hexagon Top                        | 1        | 3D Printed Part                  | [STL File](stl_files/Hexagon_Top.stl)                                                                               |
| Pulley Holder                      | 3        | 3D Printed Part                  | [STL File](stl_files/Pulley_Holder.stl)                                                                             |
| Stand_for_CAN                      | 1        | 3D Printed Part                  | [STL File](stl_files/Stand_for_CAN.stl)                                                                             |
| Stand_for_LaunchPad                | 2        | 3D Printed Part                  | [STL File](stl_files/Stand_for_LaunchPad.stl)                                                                       |
| M6 Nuts                            | 40       | McMaster Carr (P/N 91828A251)    | [External Link](https://www.mcmaster.com/91828A251/)                                                                |
| M6x16 Bolts                        | 9        | McMaster Carr (P/N 91292A135)    | [External Link](https://www.mcmaster.com/91292A135/)                                                                |
| M6x20 Bolts                        | 31       | McMaster Carr (P/N 92855A619)    | [External Link](https://www.mcmaster.com/92855A619/)                                                                |
| Acrylic Sheets                     | 1        | Needs to be cut into 3 parts     | [External Link](https://www.mcmaster.com/8560K163/)                                                                 |
| Pulley                             | 6        | Off-the-shelf component (Amazon) | [External Link](https://www.amazon.ca/V623ZZ-Groove-Bearing-Carbon-3x12x4mm/dp/B07CV8CW1F)                          |
| Velcro – 1/4 inch wide             | 50 feet  | McMaster Carr (P/N 9273K5)       | [External Link](https://www.mcmaster.com/9273K5/)                                                                   |
| FSD Sliced                         | 7        | 3D Printed Part                  | [STL File](stl_files/FSD_Sliced.stl)                                                                                |
| FSD Sliced 2                       | 7        | 3D Printed Part                  | [STL File](stl_files/FSD_Sliced_2.stl)                                                                              |
| FSD Backbone Clamp                 | 7        | 3D Printed Part                  | [STL File](stl_files/FSD_Backbone_Clamp.stl)                                                                        |
| FSD Top                            | 1        | 3D Printed Part                  | [STL File](stl_files/FSD_Top.stl)                                                                                   |
| Backbone (NiTi Tube)               | 1        | Off-the-shelf component          |                                                                                                                     |
| Tendon                             | 1        | McMaster-Carr (P/N 9442T4)       | [External Link](https://www.mcmaster.com/9442T4/)                                                                   |
| Pulley                             | 7        | Off-the-shelf component (Amazon) | [External Link](https://www.amazon.ca/V623ZZ-Groove-Bearing-Carbon-3x12x4mm/dp/B07CV8CW1F)                          |
| Shaft_GearCoupling for Tendon      | 3        | 3D Printed Part                  | [STL File](stl_files/ShaftGearCoupling_for_Tendon.stl)                                                              |
| Casing for Tendon Actuation Module | 3        | 3D Printed Part                  | [STL File](stl_files/ShaftGearCoupling_for_Tendon.stl)                                                              |
| Shaft_MotorEncoder for Tendon      | 3        | 3D Printed Part                  | [STL File](stl_files/Casing_for_Tendon_Actuation_Module.stl)                                                        |
| Ball Bearing                       | 9        | McMaster Carr (P/N 5972K910)     | [External Link](https://www.mcmaster.com/5972K91/)                                                                  |
| Motor                              | 3        | T-Motor MN4004                   | [External Link](https://store.tmotor.com/goods-438-Antigravity+MN4004+KV300+-+2PCSSET.html)                         |
| Gear_Motor                         | 3        | McMaster Carr (P/N 2662N313)     | [External Link](https://www.mcmaster.com/2662N313/)                                                                 |
| Gear_Encoder                       | 3        | McMaster Carr (P/N 2662N321)     | [External Link](https://www.mcmaster.com/2662N321/)                                                                 |
| Encoder                            | 3        | Avago AEDM-5810                  | [External Link](https://www.mouser.ca/ProductDetail/Broadcom-Avago/AEDM-5810-Z12?qs=nm95cbFn36yryX%2Fd2Onjlw%3D%3D) |
| External Retaining Ring - 8mm      | 6        | McMaster Carr (P/N 98541A116)    | [External Link](https://www.mcmaster.com/98541A116/)                                                                |
| Screw M3x10                        | 9        | McMaster Carr (P/N 91290A115)    | [External Link](https://www.mcmaster.com/91290A115/)                                                                |
| Nut M3                             | 9        | McMaster Carr (P/N 90593A001)    | [External Link](https://www.mcmaster.com/90593A001/)                                                                |
| Actuation Module                   | 1        | Assembly                         | [Link](https://github.com/ContinuumRoboticsLab/OpenCR-Hardware/tree/main/mechanics/actuation_module)                |

## Step-by-Step Instructions

For a detailed assembly guide, follow this [link to see the accompanying video](https://youtu.be/REcu881jMmQ)!

## More Information

WIP

### Further Links

[OpenCR Project](http://opencontinuumrobotics.ca)
<br/>
[Back to Top of Page](README.md)
<br/>
[Electronic Overview](electronics/README.md)
<br/>
[Hardware Overview](mechanics/README.md)

### Authors

Authors are listed in alphabetic order.

- Ankit Aggarwal
- Reinhard M. Grassmann

### License

BSD 3-Clause License

Copyright (c) 2023, Continuum Robotics Laboratory, University of Toronto

### BibTeX

This design is part of the [OpenCR Project](https://www.opencontinuumrobotics.com/).
Corresponding blog post: [Learning Kit for Tendon-driven Continuum Robots](https://www.opencontinuumrobotics.com/hands-on/2023/10/11/learning-kit.html).

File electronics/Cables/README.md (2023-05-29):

# Cables

This page provides some instructions for creating the necessary cables.

## Power wires

WIP

### Bill of Material

WIP

## Motor Phases

WIP

### Bill of Material

WIP

## Encoder cables

WIP

### Bill of Material

WIP

## CAN cables

WIP

### Bill of Material

WIP

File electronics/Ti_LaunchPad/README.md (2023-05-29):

# Ti LaunchPad

The electrical components are similar to the ones initially used by [ODRI](https://github.com/open-dynamic-robot-initiative/open_robot_actuator_hardware/blob/master/electronics/ti_electronics/README.md#texas-instruments-evaluation-board-electronics).

catchy overview

*Figure: Ti LaunchPad with two booster cards*

### Bill of Materials

| Part Name        | Quantity    | Notes                                                | File/Link                                                                                                                                                                                                                                             |  
|------------------|-------------|------------------------------------------------------|-------------------------------------------------------------------------------------------------------------------------------------------------------------------------------------------------------------------------------------------------------|   
| evaluation board | 1           | Ti LaunchPad  (LAUNCHXL-F28069M, Texas Instruments)  | [External Link (DigiKey)](https://www.digikey.ca/en/products/detail/texas-instruments/LAUNCHXL-F28069M/5138373), [External Link (Mouser)](https://www.mouser.ca/ProductDetail/Texas-Instruments/LAUNCHXL-F28069M?qs=3Lzm11LCyi87wcGMs1AZbA%3D%3D)     |
| booster          | 1 or 2      | booster card (BOOSTXL-DRV8305EVM, Texas Instruments) | [External Link (DigiKey)](https://www.digikey.ca/en/products/detail/texas-instruments/BOOSTXL-DRV8305EVM/5761583), [External Link (Mouser)](https://www.mouser.ca/ProductDetail/Texas-Instruments/BOOSTXL-DRV8305EVM?qs=Fobv33ltQGjq5TUavsUsrA%3D%3D) |
| power wire       | 1 or 2      |                                                      | [Instructions]()                                                                                                                                                                                                                                      |
| motor phase      | 1 or 2 sets |                                                      | [Instructions]()                                                                                                                                                                                                                                      |
| CAN cable        | 1           |                                                      | [Instructions]()                                                                                                                                                                                                                                      |
| Encoder cable    | 1 or 2      |                                                      | [Instructions]()                                                                                                                                                                                                                                      |

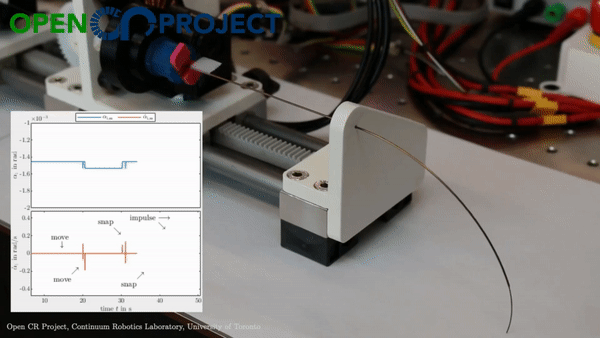
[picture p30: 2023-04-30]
mechanics/LOTR_CTCR/images/one-module-ctcr-snap.gif

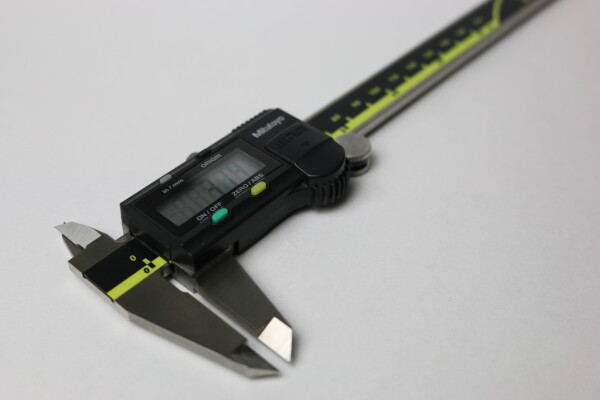
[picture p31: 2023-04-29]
mechanics/_general/images/caliper.jpg

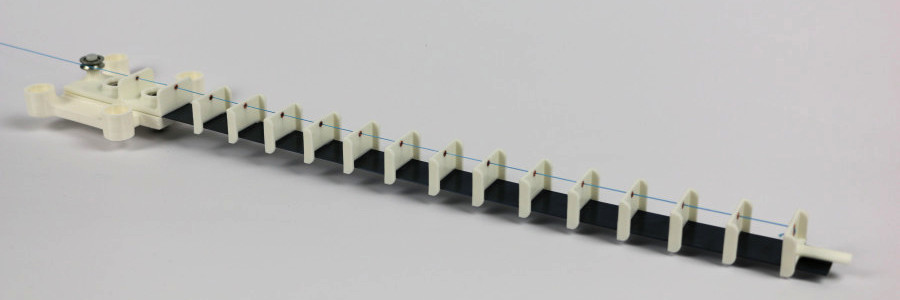
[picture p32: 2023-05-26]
mechanics/LOTR_toy_examples/Second_Toy_Example/images/second_toy_example_v.jpg

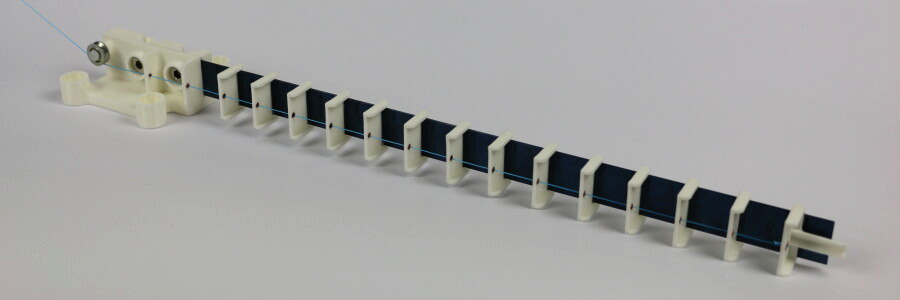
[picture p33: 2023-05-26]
mechanics/LOTR_toy_examples/Second_Toy_Example/images/second_toy_example_h.jpg

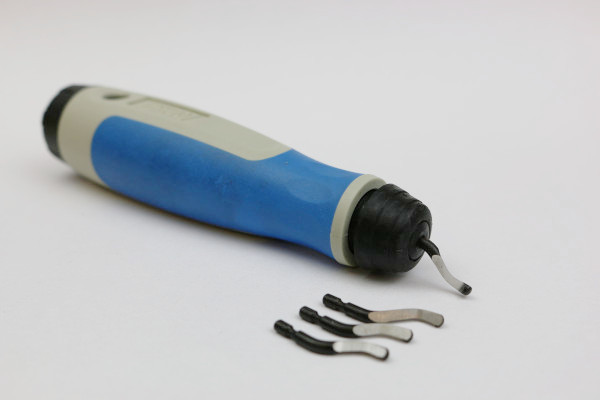
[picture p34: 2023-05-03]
mechanics/_general/images/deburring_tool.jpg

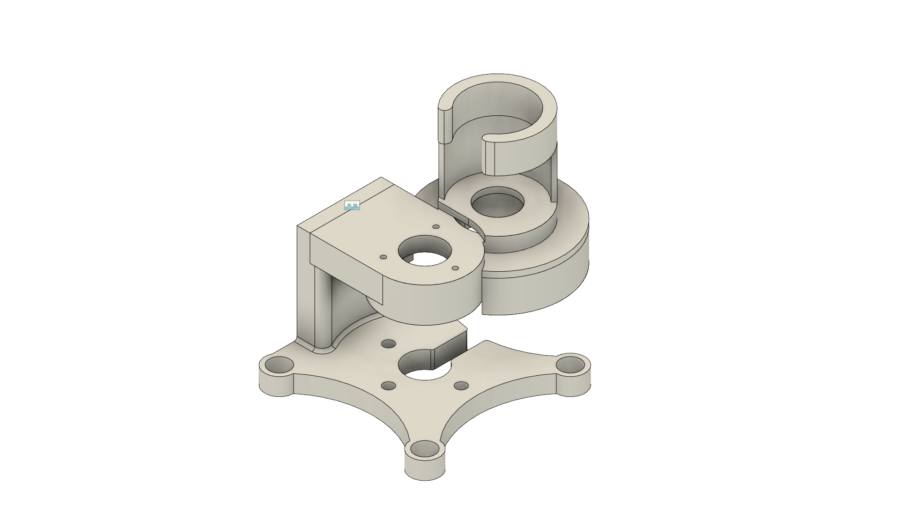
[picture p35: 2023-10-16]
mechanics/LearningKit_TDCR/images/CombinedCasing.png

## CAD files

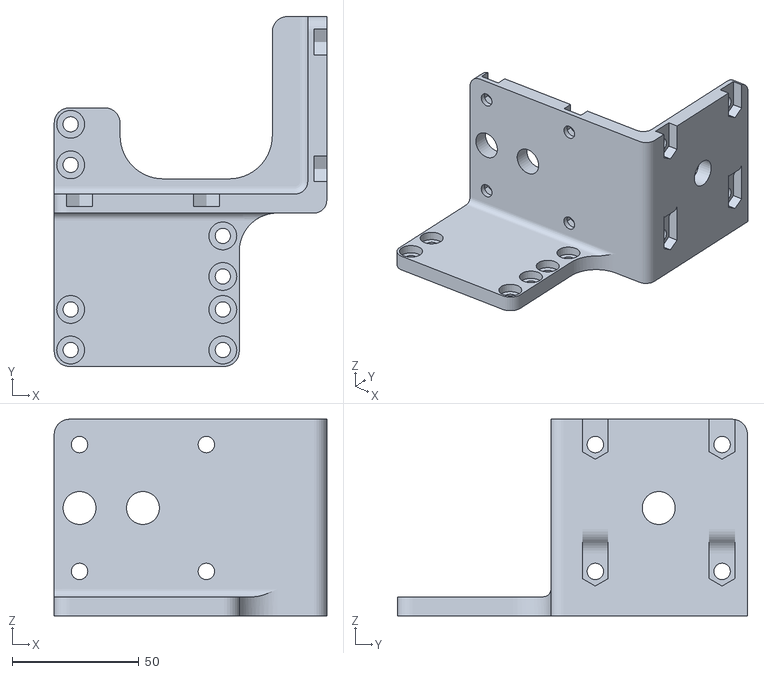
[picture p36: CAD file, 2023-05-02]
mechanics/LOTR_CTCR/stl_files/Main_Frame.stl
107.5 x 138.0 x 77.5

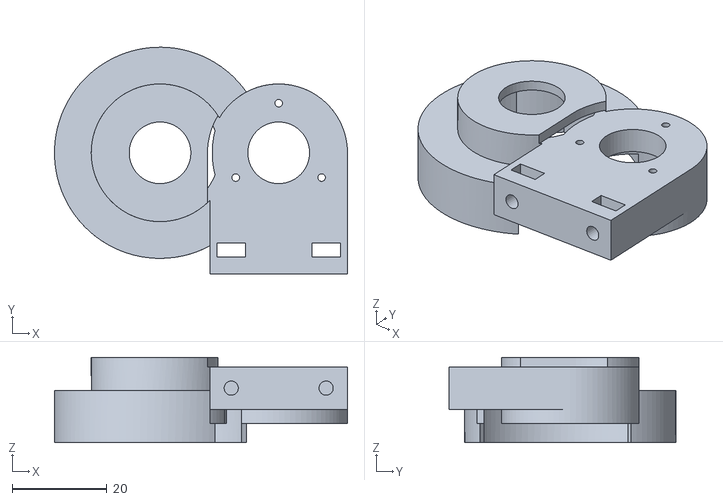
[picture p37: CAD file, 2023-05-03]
mechanics/actuation_module/stl_files/ActuationUnit_EncoderCouplingSide.stl
61.7 x 47.7 x 18.0

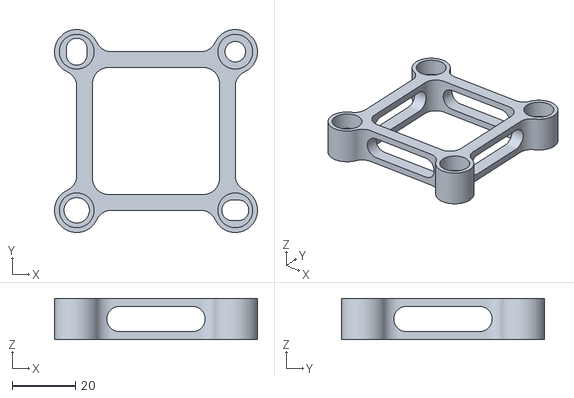
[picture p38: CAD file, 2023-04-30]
mechanics/auxiliary_hardware/stl_files/EmergencyStop_base.stl
64.0 x 64.0 x 13.0

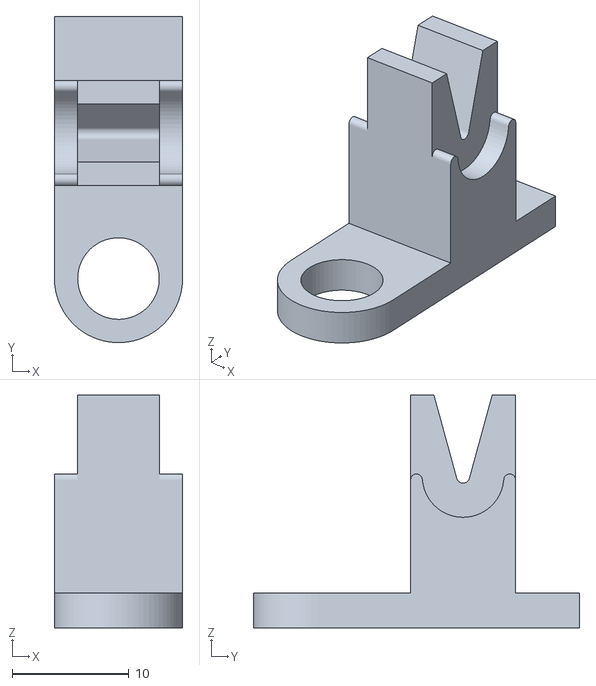
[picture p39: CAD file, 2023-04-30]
mechanics/auxiliary_tools/stl_files/FixatorDisk_OD20_13mm_Backbone_ID1.stl
11.0 x 28.0 x 20.0

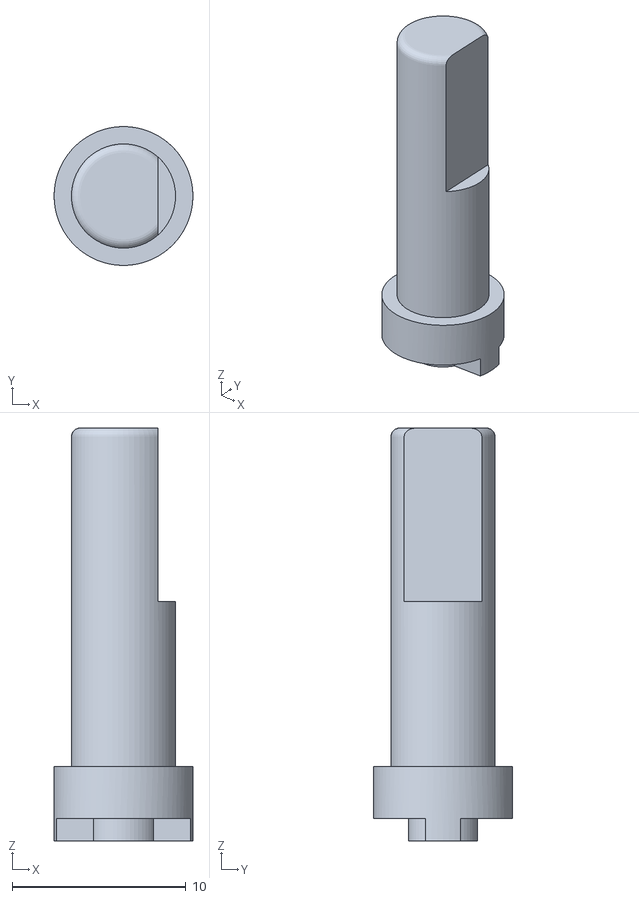
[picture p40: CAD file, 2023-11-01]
mechanics/LearningKit_TDCR/stl_files/ShaftMotorEncoder_for_Tendon.stl
8.00 x 8.00 x 23.8

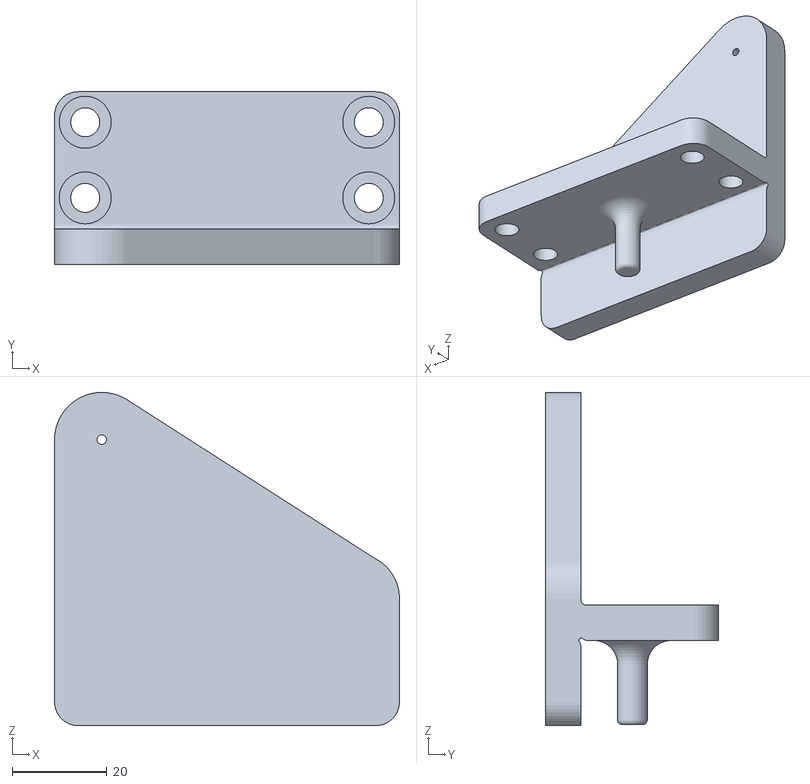
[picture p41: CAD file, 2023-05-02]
mechanics/LOTR_CTCR/stl_files/Front_Frame.stl
73.0 x 36.5 x 70.5

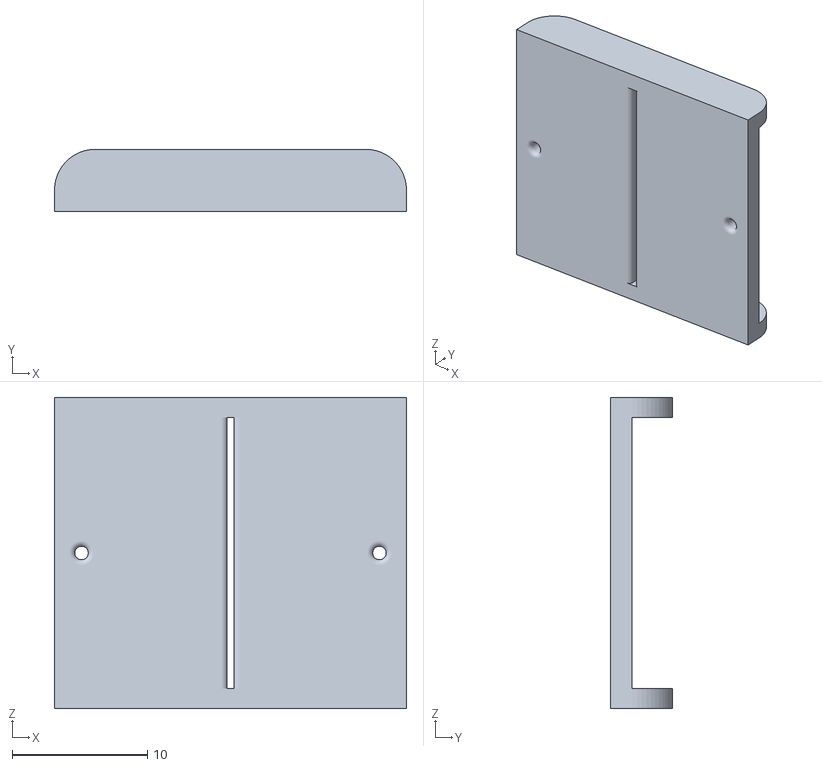
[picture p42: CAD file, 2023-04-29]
mechanics/LOTR_TDCR-planar/stl_files/spacer_disk.stl
26.0 x 4.60 x 23.0

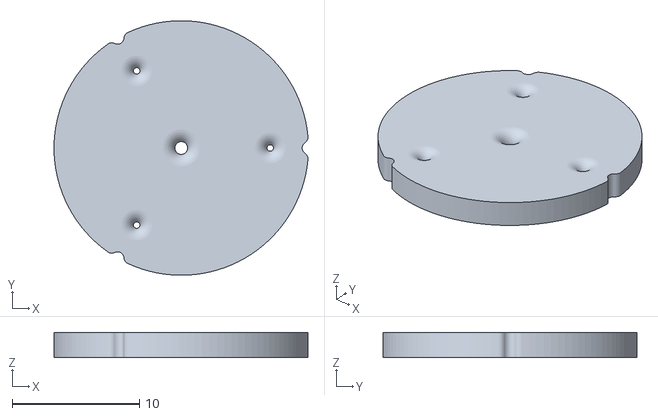
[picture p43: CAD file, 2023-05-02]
mechanics/LOTR_TDCR-spatial/stl_files/FSDzero_20mm.stl
20.0 x 20.0 x 2.00

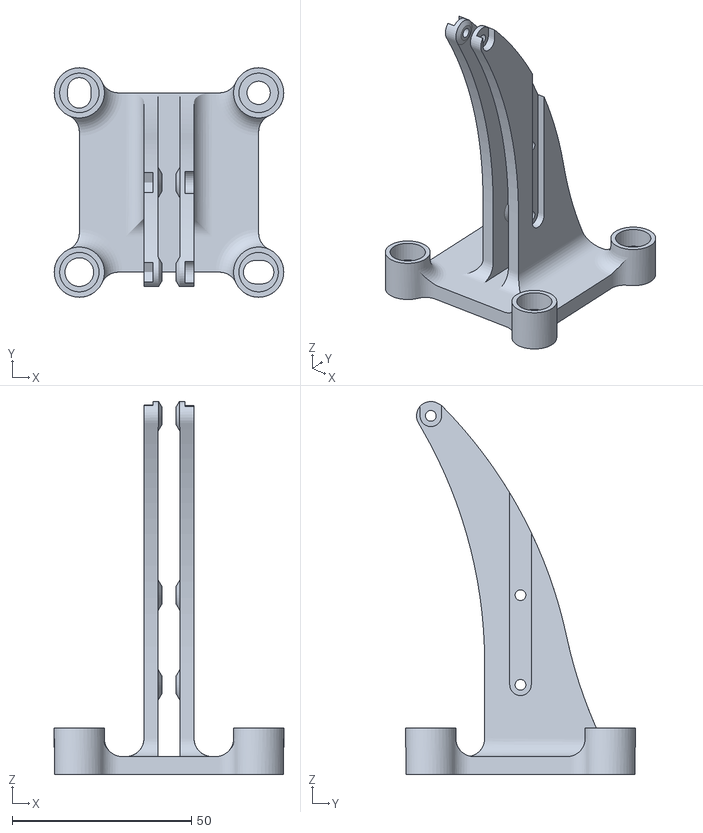
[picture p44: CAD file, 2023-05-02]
mechanics/LOTR_toy_examples/First_Toy_Example/stl_files/Stand_for_weights.stl
64.0 x 64.0 x 104.0

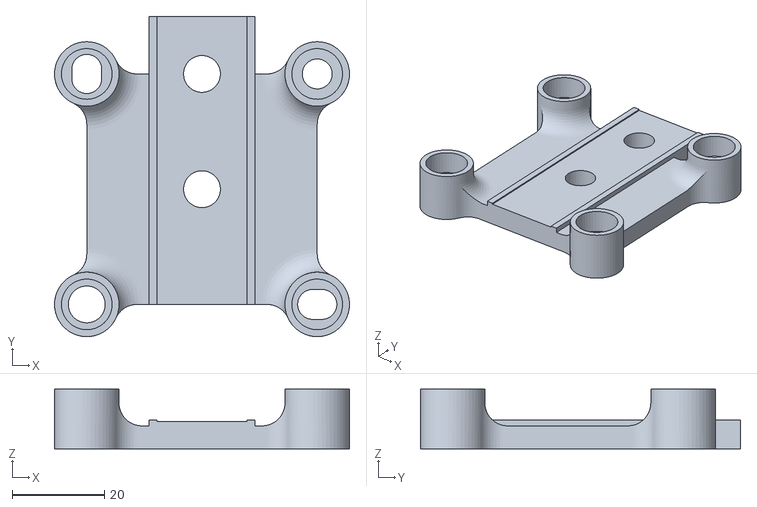
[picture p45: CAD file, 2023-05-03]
mechanics/LOTR_toy_examples/Second_Toy_Example/stl_files/Base_vertical.stl
64.0 x 69.5 x 13.0

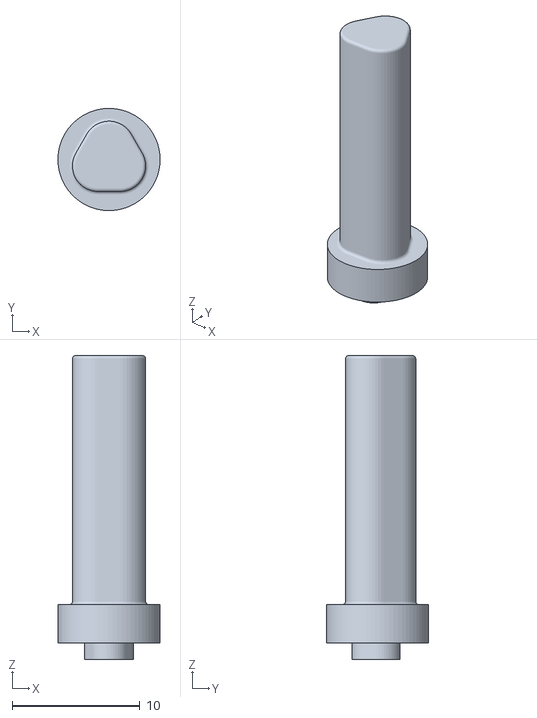
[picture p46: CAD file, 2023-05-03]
mechanics/actuation_module/stl_files/Shaft_MotorEncoder.stl
8.00 x 8.00 x 23.8

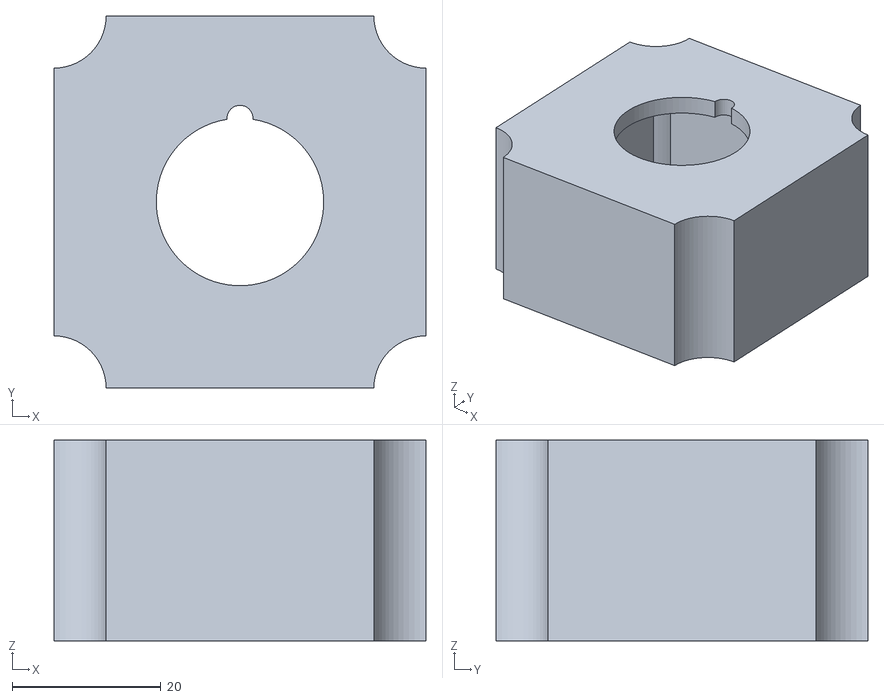
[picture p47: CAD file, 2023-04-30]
mechanics/auxiliary_hardware/stl_files/EmergencyStop_top.stl
50.0 x 50.0 x 27.0

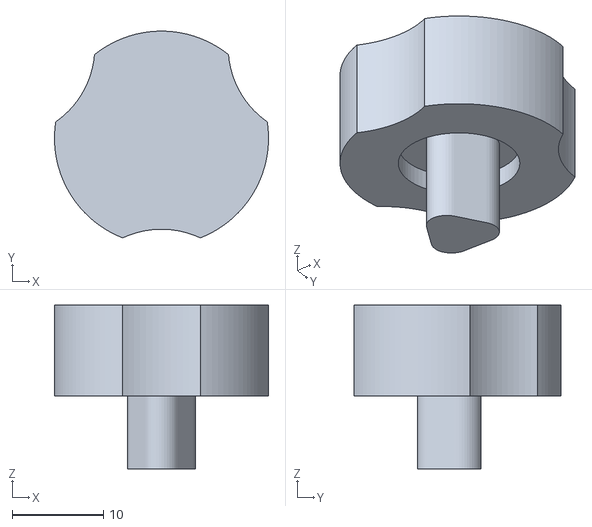
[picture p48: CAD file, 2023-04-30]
mechanics/auxiliary_tools/stl_files/BearingInsertion.stl
23.5 x 22.7 x 18.0

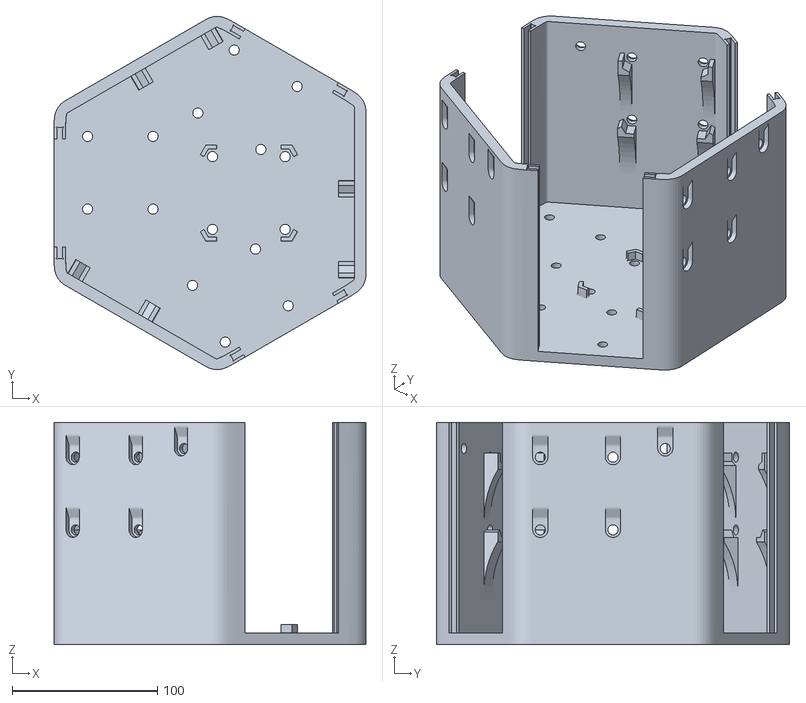
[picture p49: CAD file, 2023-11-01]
mechanics/LearningKit_TDCR/stl_files/Base_Casing.stl
214.6 x 242.8 x 153.0

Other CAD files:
mechanics/LOTR_TDCR-planar/stl_files/spacer_disk_short.stl
mechanics/LOTR_TDCR-spatial/stl_files/Tube_coppling_1mm.stl
mechanics/LOTR_toy_examples/Second_Toy_Example/stl_files/Spacer_Disk.stl
mechanics/actuation_module/stl_files/ActuationUnit_MotorSide_Cube.stl
mechanics/LOTR_CTCR/stl_files/Cap_Gear_8mm.stl
mechanics/LOTR_CTCR/stl_files/Tube_Cap.stl
mechanics/LOTR_CTCR/stl_files/Tube_coppling_0mm49.stl
mechanics/LOTR_CTCR/stl_files/Tube_coppling_0mm89.stl
mechanics/LOTR_CTCR/stl_files/Tube_coppling_1mm5.stl
mechanics/LOTR_TDCR-planar/stl_files/EE_glider_large.stl
mechanics/LOTR_TDCR-planar/stl_files/EE_glider_small.stl
mechanics/LOTR_TDCR-planar/stl_files/EE_middle.stl
mechanics/LOTR_TDCR-planar/stl_files/EE_top.stl
mechanics/LOTR_TDCR-planar/stl_files/frame_base_plate.stl
mechanics/LOTR_TDCR-planar/stl_files/frame_turret.stl
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

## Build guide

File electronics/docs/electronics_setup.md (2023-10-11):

# Sanity checks :

- 1. [Evaluation board] Code is customized for ON-ON-OFF. Check if the buttons are toggled appropriately
- 2. [Evaluation board] The jumper pin sockets must be connected for the following only : JP 6, JP 7, JP 3. All the others should be open
- 3. [Evaluation board] Make sure the encoder connection for a motor are connected to its corresponding connection on the evaluation board
- 4. Ensure that the connection between the board and the PC is oriented according to color - that H pin is connected to the CAN-H pin and the L pin is connected to the CAH-L pin. 
- 5. [Evaluation board] Encoder connection pin should have the green wire on its left
 


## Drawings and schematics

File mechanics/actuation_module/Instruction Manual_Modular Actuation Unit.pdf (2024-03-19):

# Modular Actuation Unit

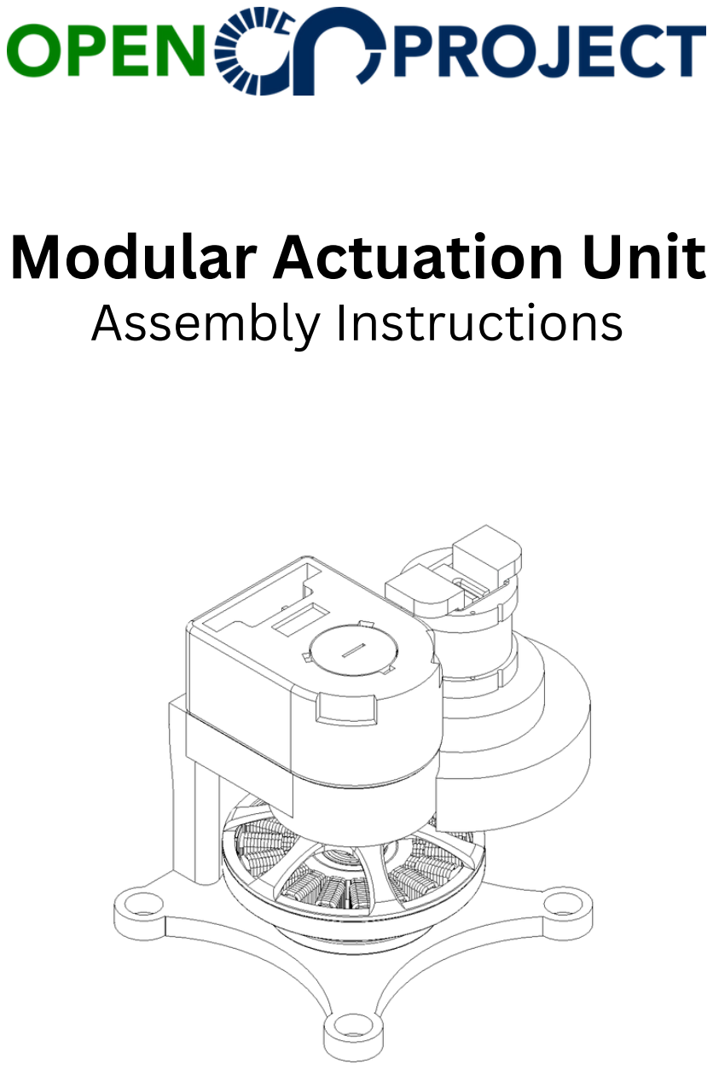
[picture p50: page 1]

# Assembly Instructions

# Exploded View

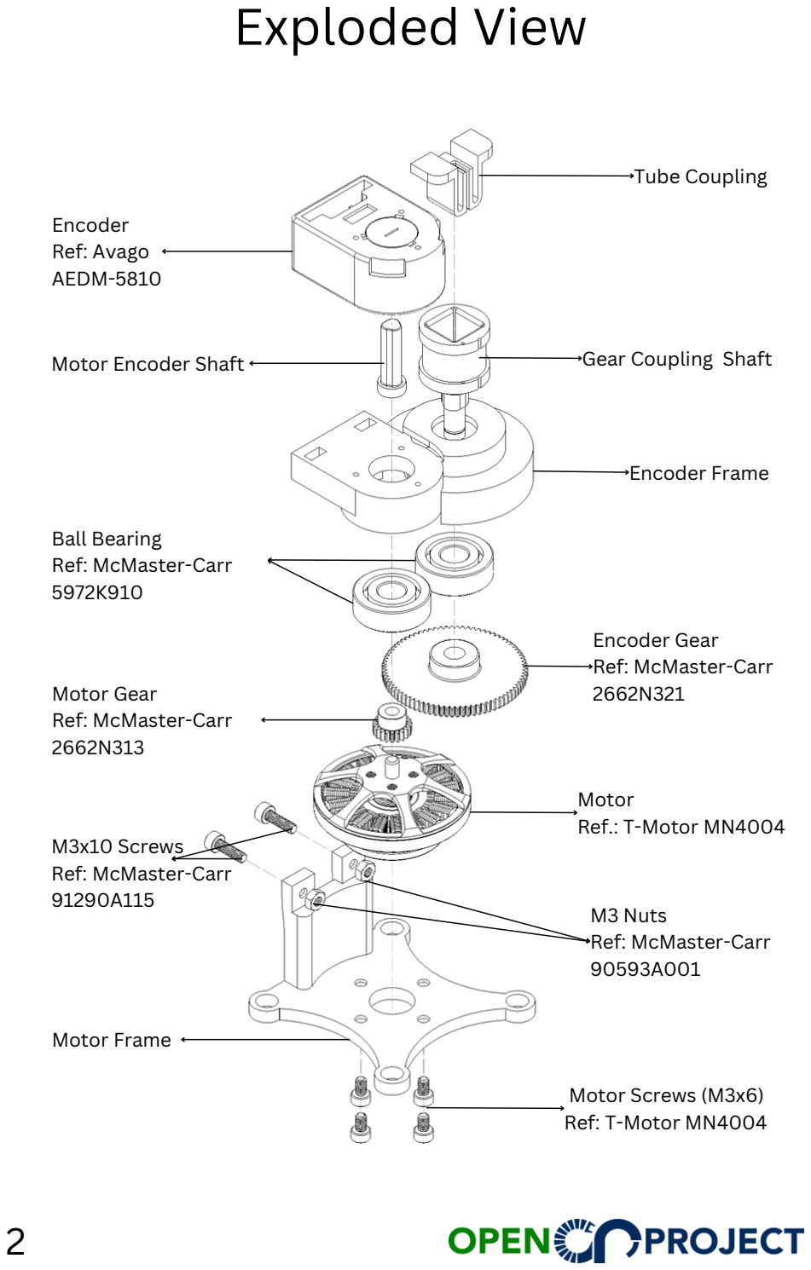
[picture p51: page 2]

Encoder
Ref: Avago
AEDM-5810

M3x10 Screws
Ref: McMaster-Carr
91290A115

Tube Coupling

Gear Coupling Shaft

Encoder Frame

Ball Bearing
Ref: McMaster-Carr
5972K910

Encoder Gear
Ref: McMaster-Carr
2662N321

Motor
Ref.: T-Motor MN4004

M3 Nuts
Ref: McMaster-Carr
90593A001

Motor Screws (M3x6)
Ref: T-Motor MN4004

Motor Encoder Shaft

Motor Gear
Ref: McMaster-Carr
2662N313

Motor Frame

# 3D Printed Parts

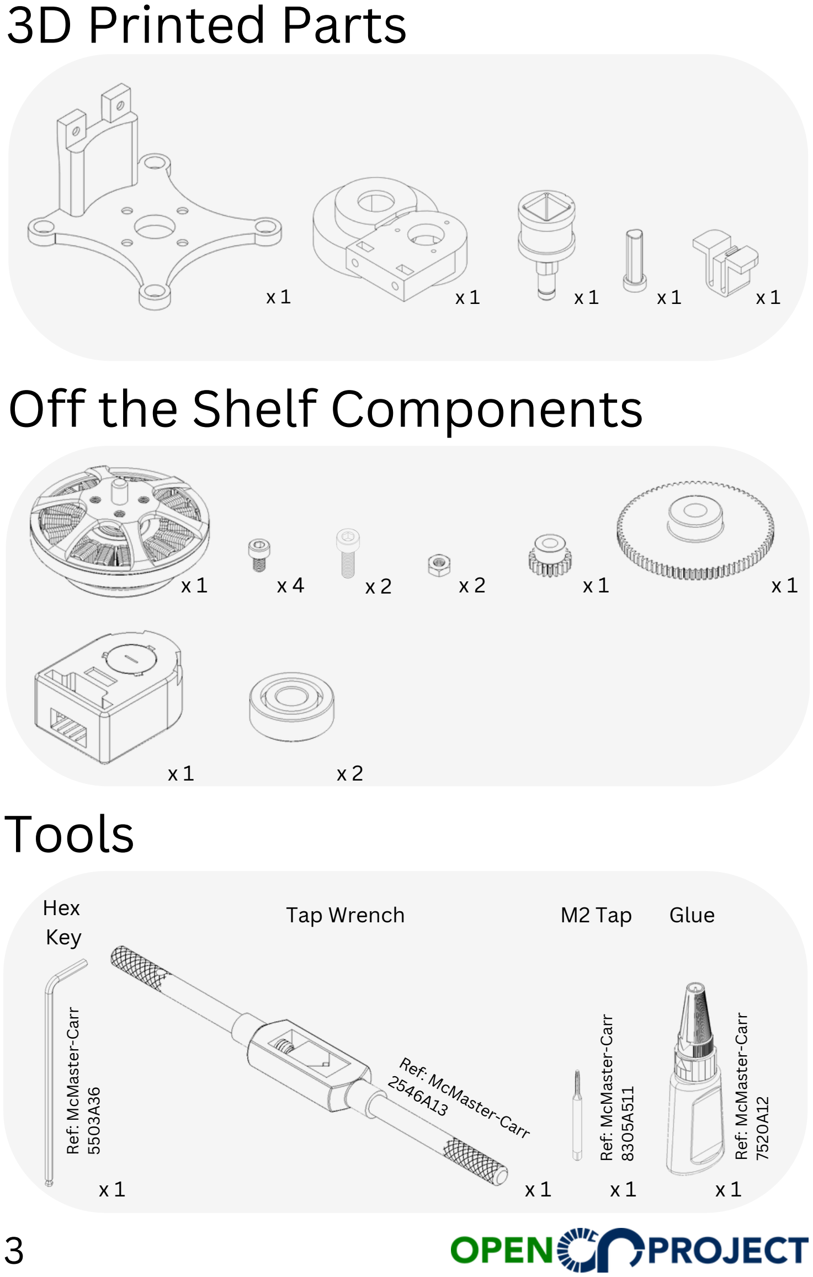
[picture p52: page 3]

x 1

# Off the Shelf Components

x 1 | x 1 | x 1 | x 1 | x 1
x 1 | x 4 | x 2 | x 2 | x 1 | x 1

x 2

x 1

x 1 | x 1 | x 1

Ref: McM

aster-C

arr

550

3

A

3

6
Ref: McM

aster-C

arr

7520

A12

Ref: McMaster-Carr
2546A13
Ref: McM

aster-C

arr

8

3

05A511

# Tools

Hex
Key
Tap Wrench | M2 Tap | Glue

# Supplementary Items

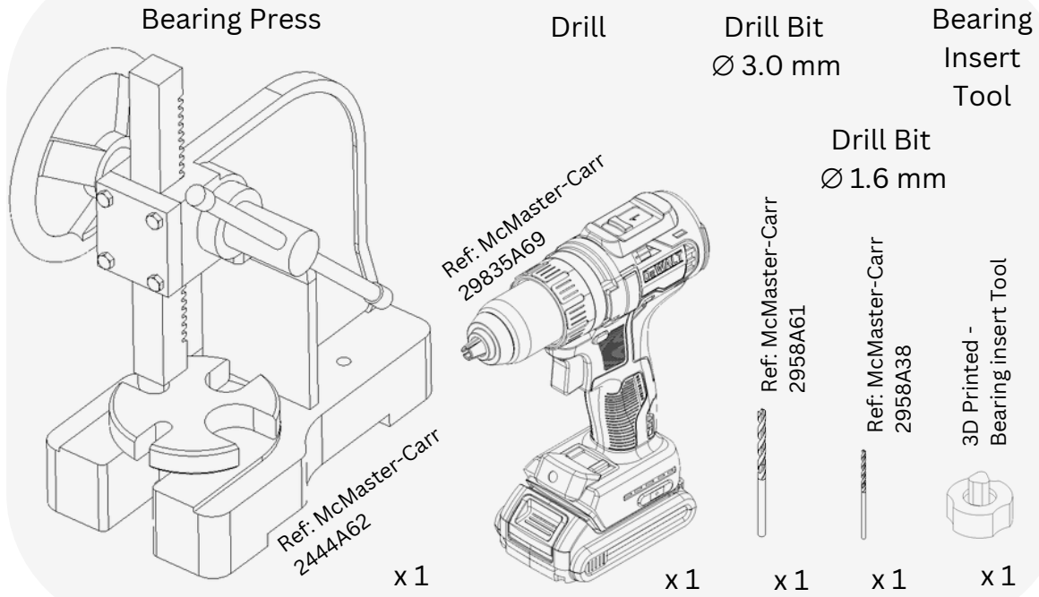
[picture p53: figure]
Ref: McMaster-Carr; Ref: McM; aster-C; arr; Printed -; Bearing insert T; Bearing Insert Tool; Bearing Press; Drill; Drill Bit; Drill Bit ⌀ 1.6 mm

# Step 1

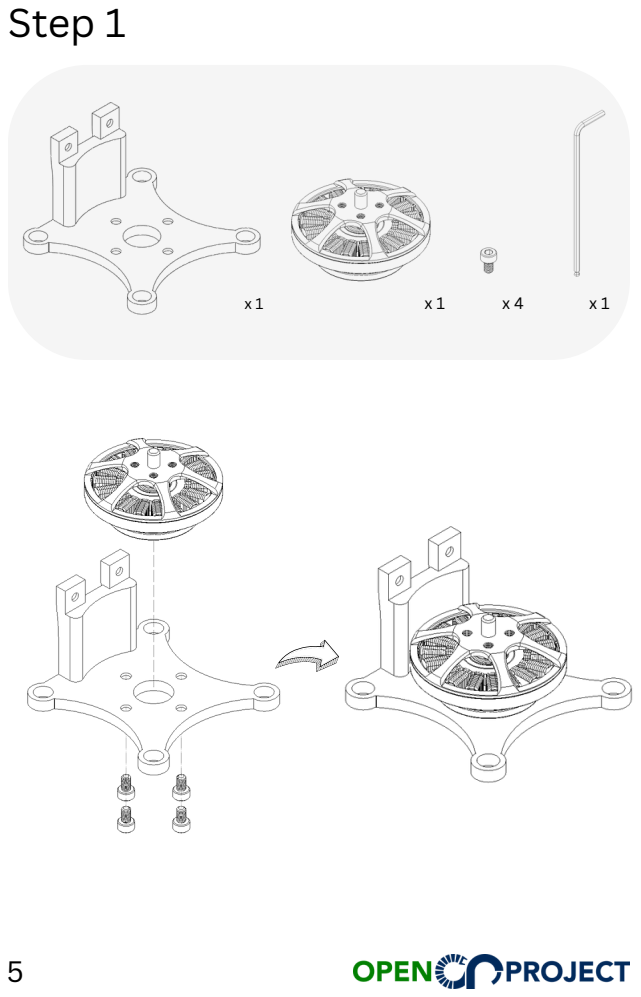
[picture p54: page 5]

# Step 2

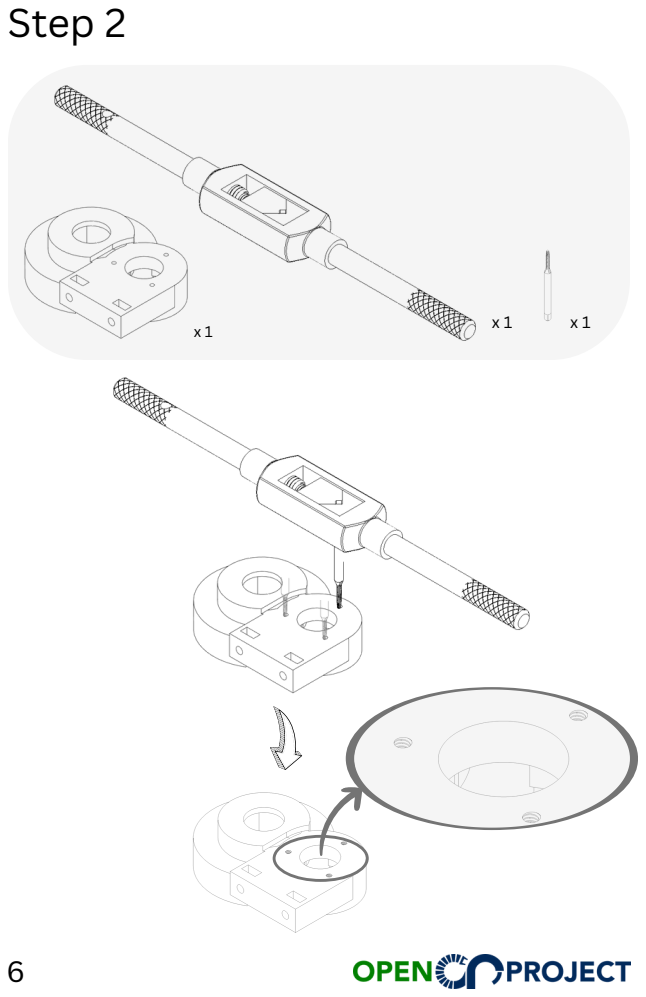
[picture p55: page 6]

# Step 3

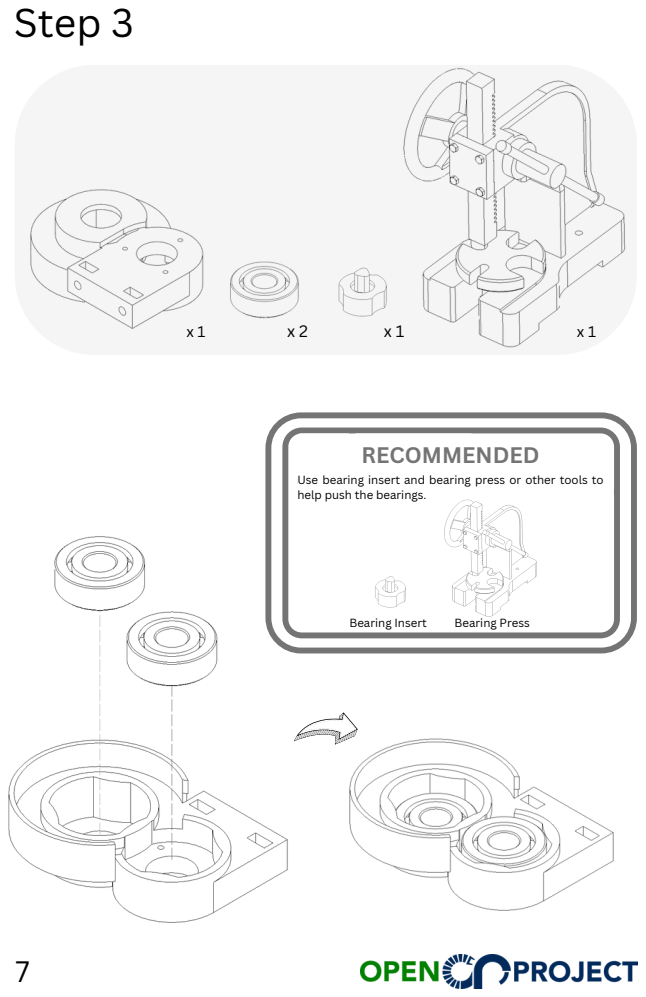
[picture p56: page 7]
RECOMMENDED; Bearing Insert; Bearing Press

Use bearing insert and bearing press or other tools to
help push the bearings.

# Step 4

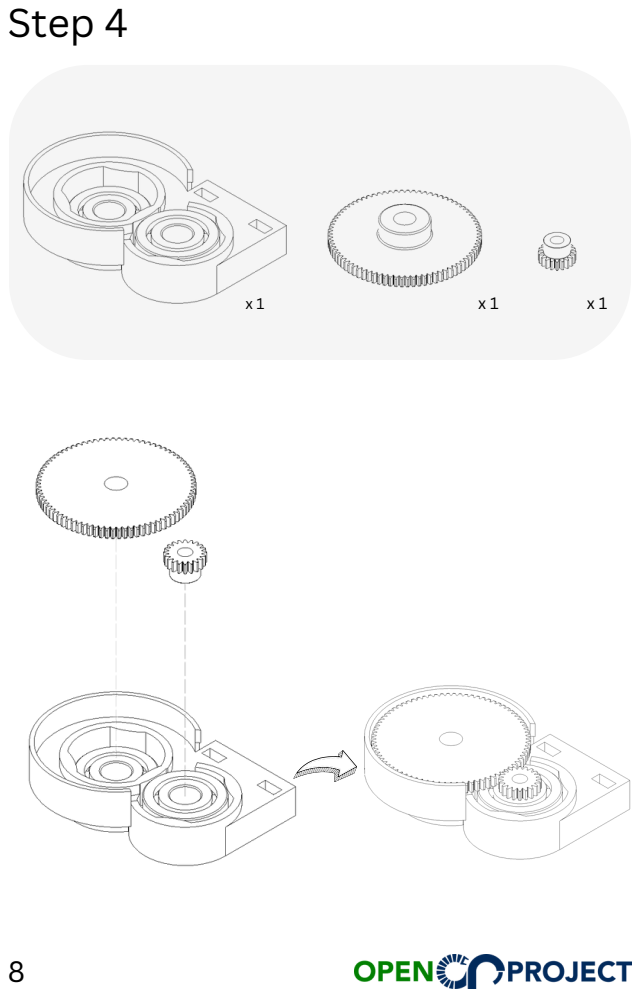
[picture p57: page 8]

# Step 5

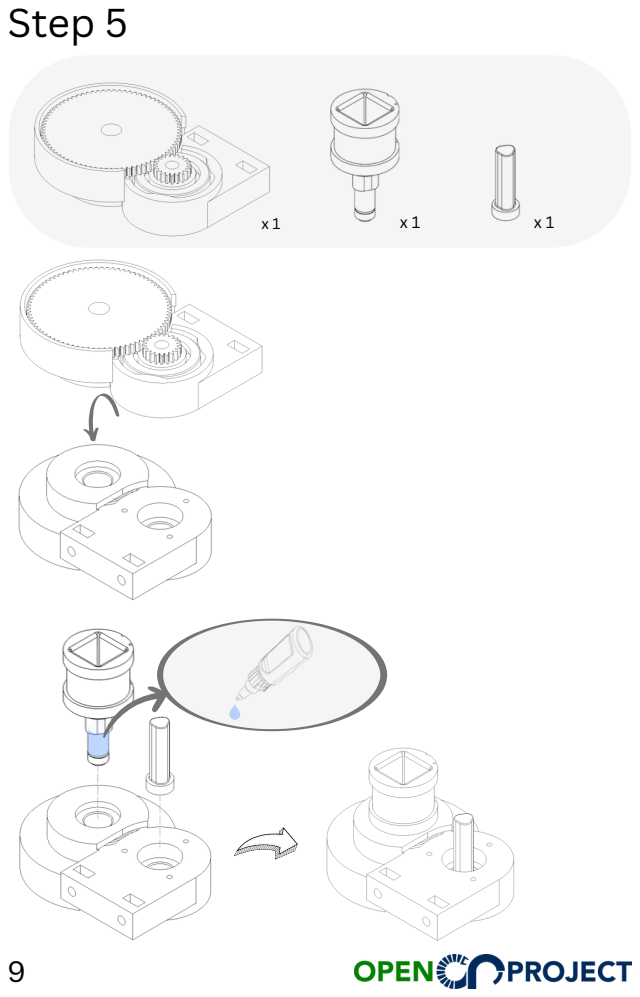
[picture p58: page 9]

# Step 6

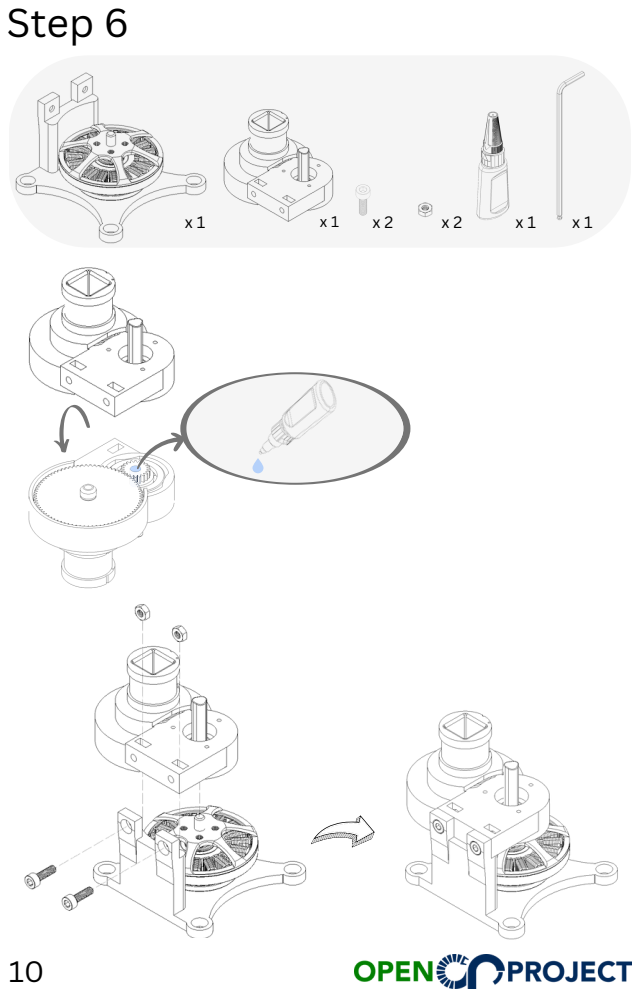
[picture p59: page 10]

# Step 7

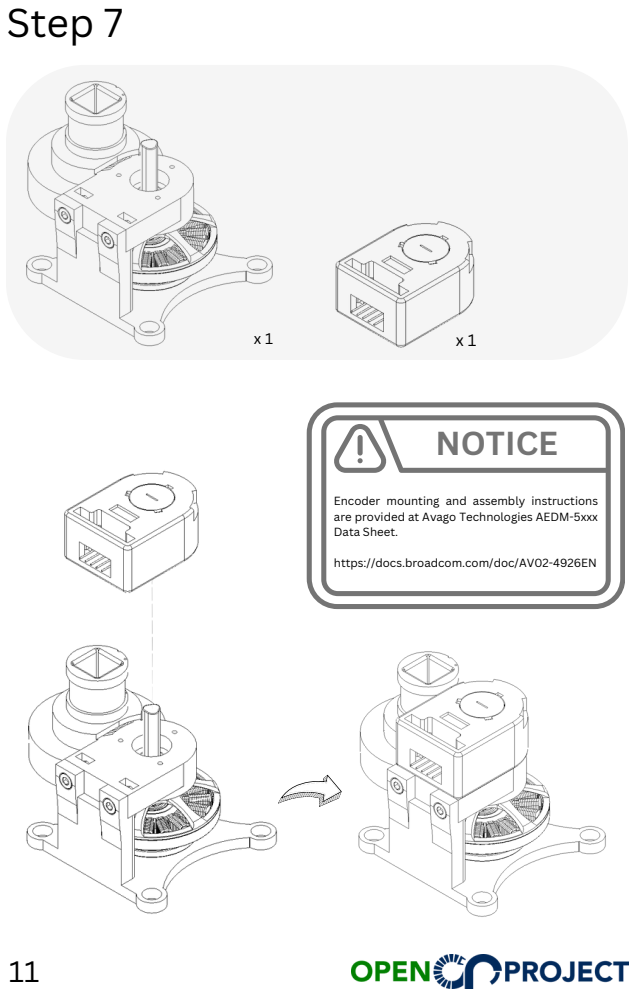
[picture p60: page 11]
NOTICE

Encoder mounting and assembly instructions
are provided at Avago Technologies AEDM-5xxx
Data Sheet.

https://docs.broadcom.com/doc/AV02-4926EN

# Step 8 - Optional

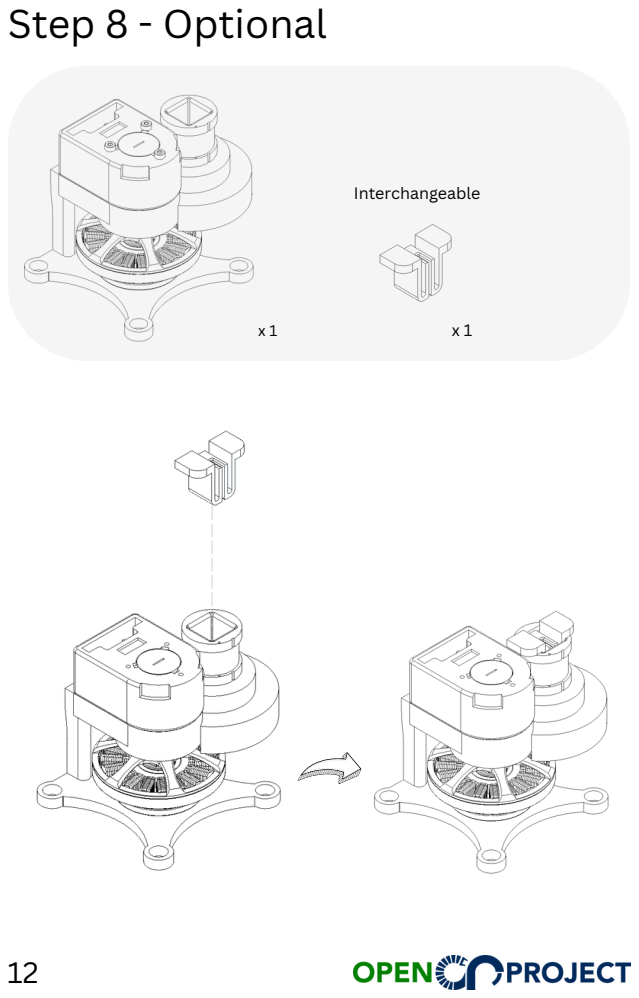
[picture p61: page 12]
Interchangeable

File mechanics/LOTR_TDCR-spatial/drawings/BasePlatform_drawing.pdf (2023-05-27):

Title; DWG No.; Rev.; Date of issue; Sheet; OpenCR Project 100

Dept. | Technical reference | Created by | Approved by

Document type | Document status

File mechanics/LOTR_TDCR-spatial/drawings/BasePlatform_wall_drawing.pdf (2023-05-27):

Title; DWG No.; Rev.; Date of issue; Sheet

Dept. | Technical reference | Created by OpenCR Project | Approved by

Document type | Document status

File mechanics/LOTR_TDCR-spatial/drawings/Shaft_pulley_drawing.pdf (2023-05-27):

Title; DWG No.; Rev.; Date of issue; Sheet; OpenCR Project 10 Ø5 12

Dept. | Technical reference | Created by | Approved by

Document type | Document status

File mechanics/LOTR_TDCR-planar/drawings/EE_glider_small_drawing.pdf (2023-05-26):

Title; DWG No.; Rev.; Date of issue; Sheet; OpenCR Project Ø76.5

Dept. | Technical reference | Created by | Approved by

Document type | Document status

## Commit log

2023-04-29 add stl files (second toy example)
    [Base_vertical.stl, Spacer_Disk.stl, Spacer_DiskEnd.stl, base_top.stl]
2023-04-29 add stl files and images (CTCR)
    [Cap_Gear_8mm.stl, Tube_Cap.stl, Tube_coppling_0mm49.stl, Tube_coppling_0mm89.stl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]
2023-04-29 add stl files and images (PCR)
    [EE_glider_large.stl, EE_glider_small.stl, EE_middle.stl, EE_top.stl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]
2023-04-30 add auxiliary dir for hardware and tools
    [BearingInsertion.stl, EmergencyStop_base.stl, EmergencyStop_top.stl, FixatorDisk_OD20_13mm_Backbone_ID1.stl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]
2023-05-02 add drawings and stl files
    [Front_Frame.stl, Main_Frame.stl]
2023-05-03 updated add drawings and stl files
    [ActuationUnit_EncoderCouplingSide.stl, ActuationUnit_MotorSide_Cube.stl, Shaft_GearCoupling.stl, Shaft_MotorEncoder.stl]
2023-05-03 fixed naming and add a new base type
    [Base_horizontal.stl, Base_vertical.stl]
2023-05-04 Add images of different prototypes
2023-05-24 Add actuation module's bill of materials
2023-05-25 Add Bill of Materials for CTCR
2023-05-25 Add files via upload
    Add Main Frame drawing
2023-05-25 Add files via upload
    Add Cap Gear 8mm drawing
2023-05-26 Add catchy image on Bill of Materials for CTCR
2023-05-26 Add Bill of Materials for TDCR Planar
2023-05-26 Add Bill of Materials for TDCR Spatial
2023-05-27 Link the drawings to Bill of Materials for TDCR Spatial
2023-05-27 Link the drawings to Bill of Materials for TDCR-Planar
2023-05-27 Edit notes of Bill of Materials for TDCR-Planar
2023-05-29 Add step-by-step CTCR Assembly
2023-05-29 init Cables
2023-05-29 added links to prototypes' README.md
2023-05-29 Add step-by-step instruction for TDCR-spatial assembly
2023-10-16 Add Learning Kit
    [Base_Casing.stl, FSD_Sliced _1.stl, FSD_Sliced_2.stl, FSD_Top.stl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]
2023-10-31 Compressed STL of CTCR assembly
    STL file is 52 MB big. I had to compress it under 25 MB.
2023-11-01 improve text description
    [Base_Casing.stl, Casing_for_Tendon_Actuation_Module.stl, FSD_Backbone_Clamp.stl, FSD_Sliced.stl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]
